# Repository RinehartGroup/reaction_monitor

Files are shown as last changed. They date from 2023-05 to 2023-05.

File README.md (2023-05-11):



# reaction_monitor
An Arduino-based data logger for logging temperature, gas flow, and gas composition data from chemical reactions.

## Motivation

Establishing meaningful trends and building physically meaningful models based on the analysis of nanomaterials requires that those materials be synthesized under carefully controlled, reproducible conditions. In many cases, however, the true reaction conditions are far more complex than is easily conveyed in the simplified narrative form of a publication experimental data section. In our initial trials of standardizing our raw data formats we isolated several key parameters of interest for real-time monitoring: reaction temperature, gas flow rate, and gas composition (for N<sub>2</sub>/O<sub>2</sub> mixtures). While such systems are likely common at scale, we sought to use readily available components (many of which are common in academic research labs or are otherwise low-cost) to automate data logging in a varatile and nominally modular fashion that would be amenable to a small-scale, rapidly changing research environment.

## Overview

<p align="center">
    reaction monitor setup
</p>

The heart of the reaction monitor is an Arduino Mega. The Arduino communicates with an [Omega PID controller](https://www.omega.ca/en/control-monitoring/controllers/pid-controllers/p/CN7200-Series) via its MODBUS serial interface. [Gas flow](https://www.mcmflow.com/product/model-100/) and [oxygen sensors](https://www.apogeeinstruments.com/so-110-soil-response-thermistor-reference-oxygen-sensor/) output 0 - 3.3 V signals which are read by [16-bit ADCs](https://www.adafruit.com/product/1085) and sent to the Arduino via the I2C protocol. 

Two oxygen sensors are available and are intended to be put before and after the reaction. In this initial implementation, a pure or mixed gas is bubbled throiugh through a solution containing the reactive species, such that the first oxygen sensor (OXY1) is calibrated under dry conditions and the second (OXY2) is calibrated under wet conditions. The Arduinio logs raw voltages from the sensors in addition to the calculated oxygen percentages, so oxygen percentages can always be recalculated during data workup (as is done in the [example data workup](sample_data_workup.ipynb)). The calibration procedure for the oxygen sensors are available in the [Apogee manual](assets/SO-100-200-manual.pdf), and our calibration data for both wet and dry conditions are available in [/calibration](calibration). The oxygen percentage calculations account for humidity. In our Arduino code, we assume 0% humidity for OXY1 as it measures a gas mixture directly from cylinders with dry gas. We placed a [temperature, pressure and humidty sensor](https://www.adafruit.com/product/2652) after OXY2 to calculate the post-reaction oxygen percentage. The humidity sensor is placed in a 3D printd enclosure available in [/materials](materials)

The electronics are housed in a 3D printed enclosure, also available in [/materials](materials). The enclosure includes two LCDs displaying basic information on oxygen percentages, gas flow rates, time, PID values (process value, set value, and output), and, when recording data, the name of the file being written. Data is recorded to a micro SD card. Recording is started/stopped by pressing the button on the front of the enclosure. When recording, a red LED will be lit and a blue LED will flash each time a data point is collected (which is every second in the current code).

<p align="center">
    labeled reaction monitor
</p>

## Example Usage

The [example data workup notebook](sample_data_workup.ipynb) uses data file [RXN00026.CSV](sample_data/RXN00026.CSV). This data was collected during a reaction which followed the procedure detailed in [Kirkpatrick _et al._ Size-Tunable Magnetite Nanoparticles from Well-Defined Iron Oleate Precursors, Chemistry of Materials, 2022](https://pubs.acs.org/doi/10.1021/acs.chemmater.2c02046) ([free copy here](https://drive.google.com/file/d/1hveF1zS2nrNvON7UYBfMMZ2yYlZfvH2g/view)). In short, the synthesis of magnetite nanoparticles uses a reduced pressure atmosphere, then an N<sub>2</sub> atmosphere during the initial heating of the reaction mixture. Once the reaction is under reflux a small amount of oxygen is introduced into the gas mixture. The size, shape, and presence/absence of core / shell structures involving wustite and magnetite can be affected by precise control of the gas flow, composition, and temperature profile. The reaction monitor records every aspect of these reaction conditions, including any user-intervention with the PID controller.

<p align="center">
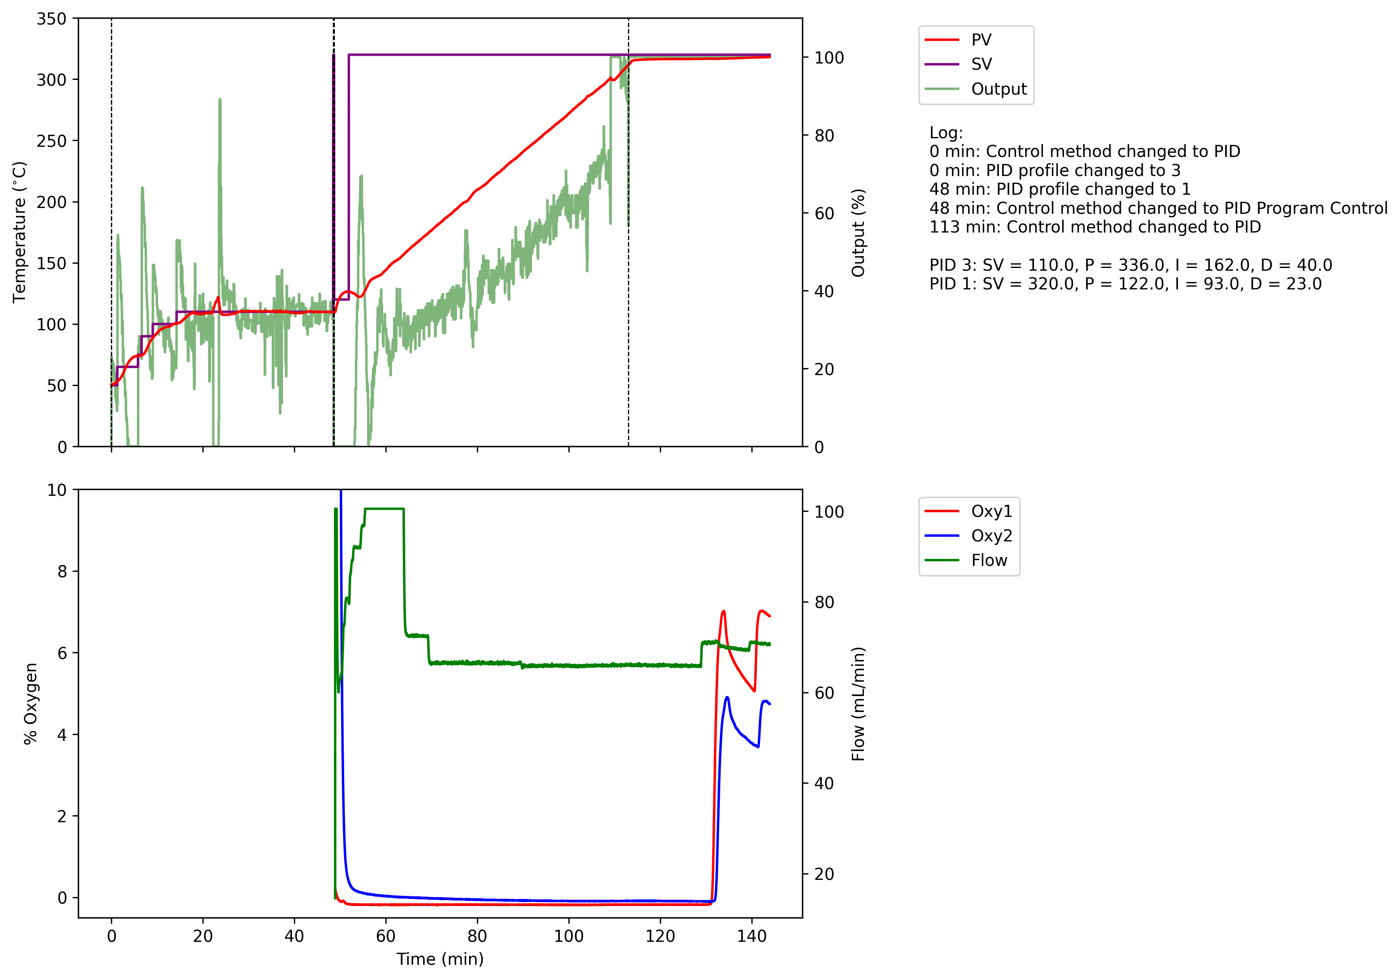
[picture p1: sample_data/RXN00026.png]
sample reaction data workup
    
</p>

## Future Work

While our primary goal was to provide automated data logging, initial data indicates the possibility of automating key decision points in chemical reactions, thus eliminating hidden sources of uncontrolled human intervention. In the usage example above, our results indicate that the timing of introducing O<sub>2</sub> into the reaction affects the phase purity of the final particles. Presently, O<sub>2</sub> is introduced when the chemist running the reaction visually detects the onset of solvent reflux. The data provided by the reaction monitor has the potential to solidify this association between O<sub>2</sub>, reflux, and particle quality and allow us to begin the process of optimizing an automatic trigger for flow adjustment. In this specific example, the trigger would be a function of the slope of the output tracking temperature control. This data corresponds to the power being used toward resistive heating (on a 0-100 scale). In the sample data, the start of reflux can be seen at the point where output is persistently at 100 and the process value (PV) is relatively constant and unable to reach the set value (SV) which is chosen to correspond to a temperature above the reflux temperature of the solution. Implementing this change would require replacing the passive gas sensors with mass flow controllers, allowing for both monitoring and control of the reaction conditions.

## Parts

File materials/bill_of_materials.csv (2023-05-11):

item | quantity | cost | link
Arduino Mega | 1 | 48.4 | https://store-usa.arduino.cc/products/arduino-mega-2560-rev3
16x2 LCD Display (I2C) | 2 | 11.99 | https://www.amazon.com/GeeekPi-Character-Backlight-Raspberry-Electrical/dp/B07S7PJYM6
DS3231 Precision RTC Breakout (I2C) | 1 | 17.5 | https://www.adafruit.com/product/3013
Micro SD Breakout Board (SPI) | 1 | 11.99 | https://www.amazon.com/FainWan-Storage-Expansion-Interface-Adapter/dp/B09JZC6TCD
ADS1115 16-Bit ADC - 4 Channel with Programmable Gain Amplifier (I2C) | 2 | 14.95 | https://www.adafruit.com/product/1085
BME280 I2C or SPI Temperature Humidity Pressure Sensor | 1 | 14.95 | https://www.adafruit.com/product/2652
LM2596 DC to DC Buck Converter | 1 | 8.99 | https://www.amazon.com/LM2596-Converter-3-0-40V-1-5-35V-Supply/dp/B08NV3JCBC
12V 2A AC Adapter | 1 | 11.99 | https://www.amazon.com/Adapter-Charger-Replacement-Regulated-Transformer/dp/B0852HX9HV
Apogee SO-110 Soil Response Thermistor Reference Oxygen Sensor | 2 | 365 | https://www.apogeeinstruments.com/so-110-soil-response-thermistor-reference-oxygen-sensor/
McMillan Flow Model 100-3 Gas Flow Sensor 20-100 mL/min | 1 | 275 | https://www.mcmflow.com/product/model-100/
McMillan Flow Model 100-5 Gas Flow Sensor 100-500 mL/min | 1 | 275 | https://www.mcmflow.com/product/model-100/
Omega CN7200 PID Controller | 1 |  | https://www.omega.ca/en/control-monitoring/controllers/pid-controllers/p/CN7200-Series
MD-30 CONN PLUG MALE MINI DIN 3P SLDR | 5 | 2.29 | https://www.digikey.com/en/products/detail/cui-devices/MD-30/96910
MD-30SP CONN RCPT FMALE MINI DIN 3P SLDR | 5 | 2.54 | https://www.digikey.com/en/products/detail/cui-devices/MD-30SP/165983
MD-70 CONN PLUG MALE MINI DIN 7P SLDR | 2 | 2.51 | https://www.digikey.com/en/products/detail/cui-devices/MD-70/96918
MD-70SP CONN RCPT FMALE MINI DIN 7P SLDR | 2 | 2.75 | https://www.digikey.com/en/products/detail/cui-devices/MD-70SP/135497
Barrel Jack Connector - Female | 1 | 9.99 | https://www.amazon.com/DaierTek-5-5x2-1mm-Female-Connector-Barrel/dp/B096XJWZJQ
Chemical-Resistant Gasket; Fluoroelastomer, for 1" Tube OD | 1 | 3.2 | https://www.mcmaster.com/5044K53/

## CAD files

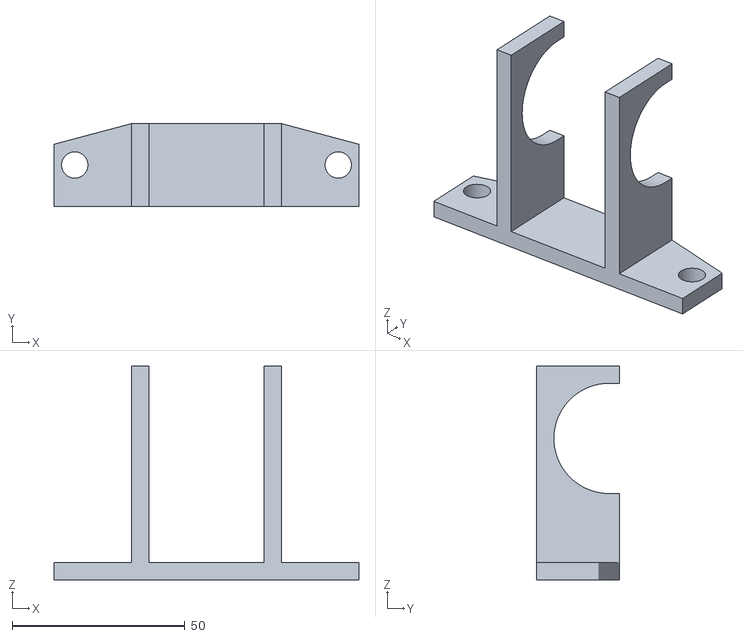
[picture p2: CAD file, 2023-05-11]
materials/humidity_sensor_housing_pegboard_adapter.stl
88.2 x 23.9 x 61.9

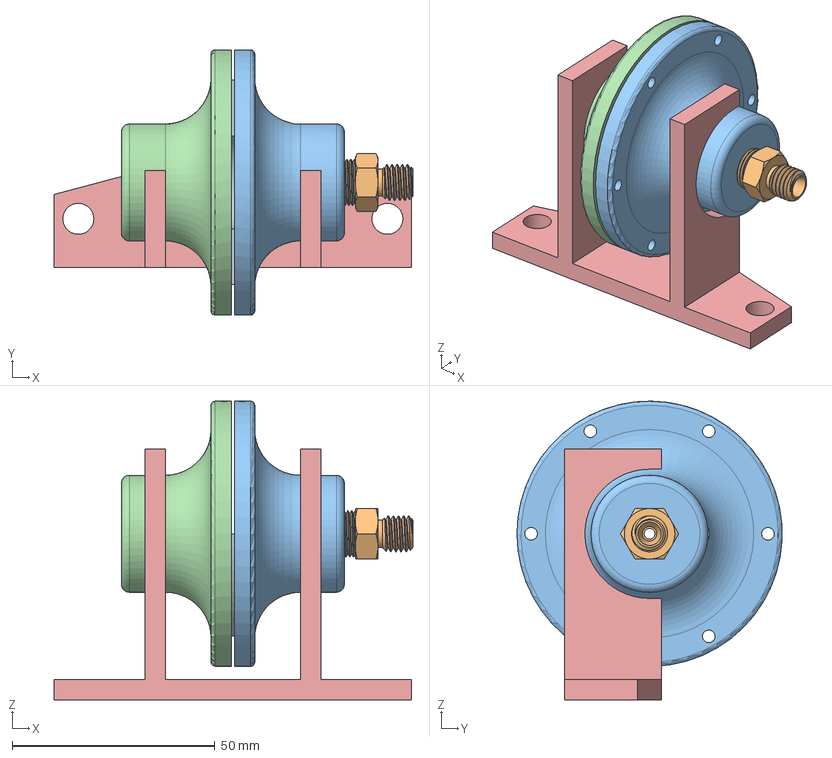
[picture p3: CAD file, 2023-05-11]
materials/humidity_sensor_housing.step
88.5 x 65.4 x 73.6 mm
5044K53_Chemical-Resistant Gasket
5272K292
scaled_part

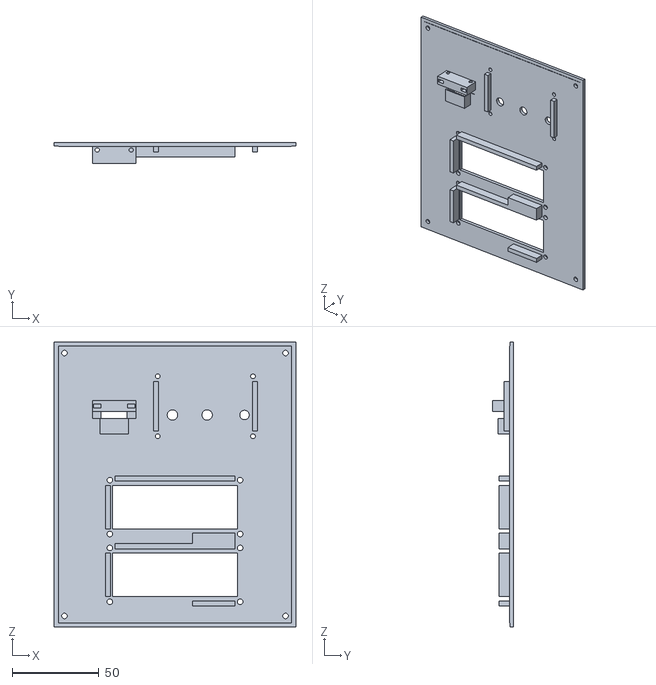
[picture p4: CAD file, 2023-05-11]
materials/reaction_monitor_enclosure_lid.stl
139.0 x 12.0 x 164.0

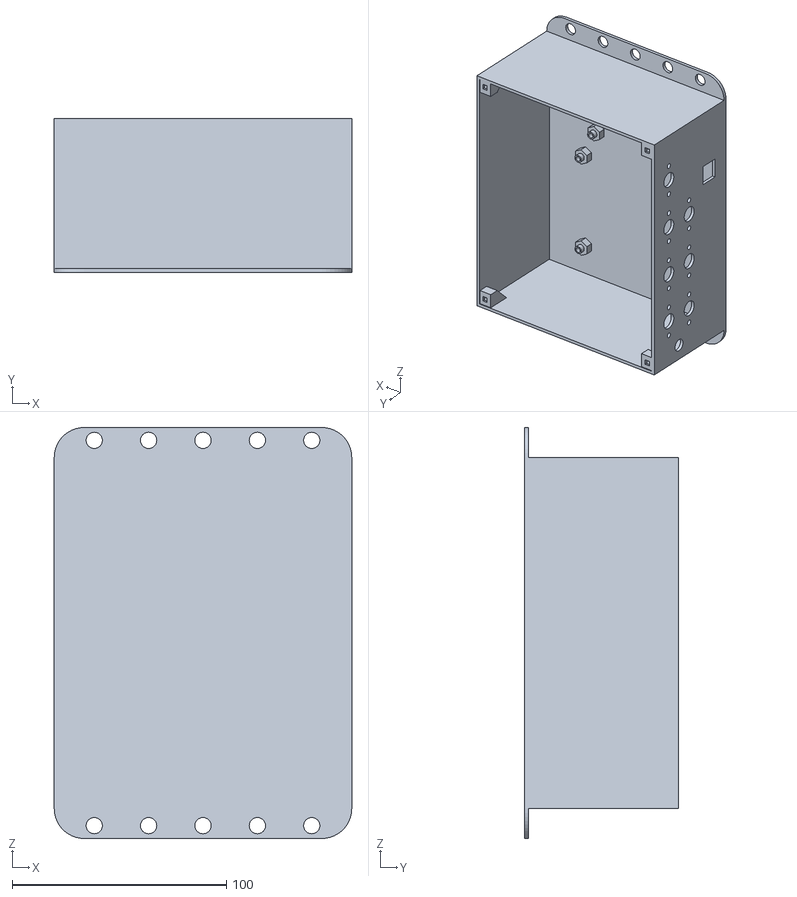
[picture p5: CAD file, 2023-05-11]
materials/reaction_monitor_enclosure_base.stl
139.0 x 72.0 x 192.0

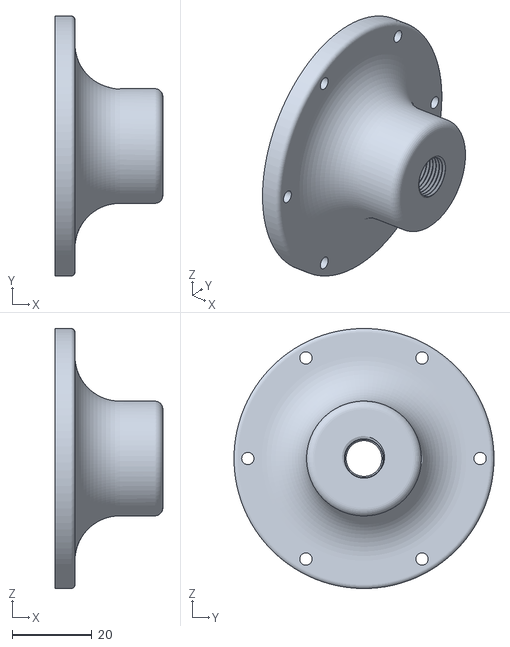
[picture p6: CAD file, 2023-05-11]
materials/humidity_sensor_housing_side1.stl
27.1 x 65.4 x 65.4

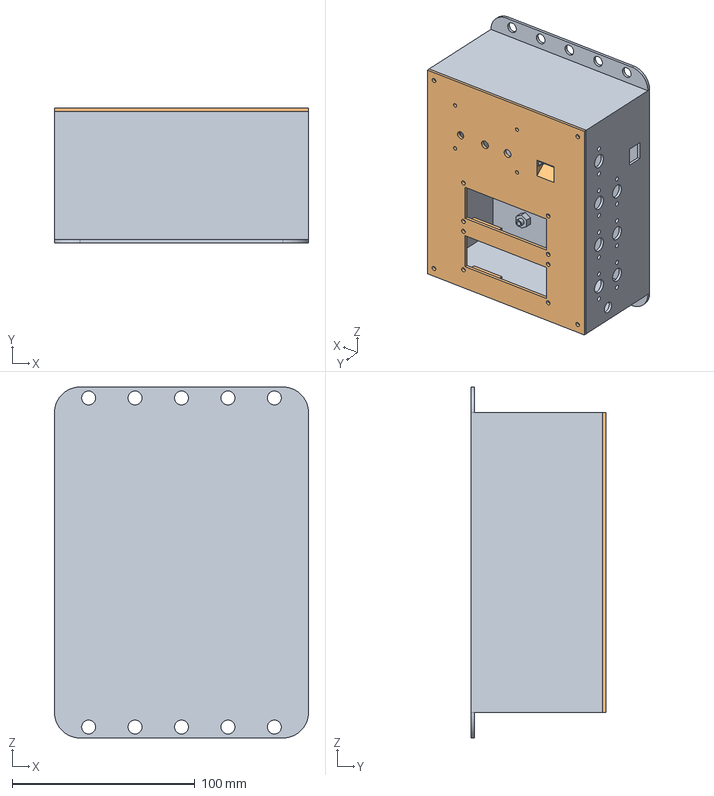
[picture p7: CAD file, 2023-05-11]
materials/reaction_monitor_enclosure.step
139.0 x 74.0 x 192.0 mm

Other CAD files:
materials/humidity_sensor_housing_side2.stl
materials/humidity_sensor_housing.f3z
materials/reaction_monitor_enclosure.f3d

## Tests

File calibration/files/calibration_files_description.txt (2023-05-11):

RXN00009.CSV; dry air; Sensors in sealed container with air and Drierite;
RXN00010.CSV; atmospheric; Sensors open to atmosphere;
RXN00011.CSV; wet air; Sensors in sealed container with water in bottom;
RXN00012.CSV; dry N2 no humidity sensor; Note: this had the humidity sensor unattached. Use RXN00016 instead;
RXN00015.CSV; wet N2; N2 stream through bubbler, then the two oxygen sensors, then the BME280 sensor;
RXN00016.CSV; dry N2; N2 stream straight to oxygen sensors then the BME280 sesnor;

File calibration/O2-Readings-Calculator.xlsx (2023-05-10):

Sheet: Sheet1
 | Sensor Model: SO- |  |  | Units |  | Yellow Cells = Requested Information
Calibration Info | Calibration mV Reading |  |  | mV
 | Calibration Air Temperature |  |  |  |  |  | SO-110, 120 Constants | SO-210, 220 Constants
 | Calibration Humidity |  |  | % |  | C1 | -0.06949 | -0.0361 | C3
 |  | Calibration Elevation |  |  |  | C2 | 0.001422 | 0.001896 | C2
 |  | Calibration Pressure |  | kPa |  | C3 | -8.213e-07 | -4.333e-06 | C1
Sample Info | Sample mV Reading |  |  | mV |  | Cal. Vapor Pressure |  | Sample Vapor Pressure
 | Sample Air Temperature |  |  |  |  | 0.000 |  | 0.000
 | Sample Humidity |  |  | % |  | Cal. Sat. Pressure |  | Samp. Sat Pressure
 |  | Sample Elevation |  |  |  | 0.152 |  | 0.152
 |  | Sample Pressure |  | kPa |  | Cal. Barr. Pressure |  | Samp. Barr. Pressure
Offset |  |  |  |  | 0.3 | 101.325 |  | 101.325
 |  |  |  |  |  | Calibration Temperature Coefficient
 |  |  |  |  |  | -1.265
Output and Correction Options
 | Calibration Factor (Multiplier) |  |  |  | -69.833 | CF = Correction Factor
 | Calibration Offset |  |  |  | 20.950 | mVc = mV at calibration
 |  |  |  |  |  | mV0 = mV at zero
 | Uncorrected Oxygen Reading [%] |  |  |  | 20.950 | CO = Calibration Offset
 |  |  |  |  |  | PB = Barrometric Pressure (kPa)
 |  |  |  |  |  | E = Elevation
 |  |  |  |  |  | O2 = Final O2 Reading
 |  |  |  |  |  | O2m = Uncorrected O2 Reading
 | Final Sample Oxygen Reading [%] |  |  |  | 20.950 | PBC = Barrometric Pressure (Calibration) [kPa]
Formulas for SO-110, 120, 210, 220 and Calculations |  |  |  |  |  | PBM = Barrometric Pressure (Sample) [kPa]
 |  |  |  |  |  | TS = Air Temperature (Sample)
 |  |  |  |  |  | TC = Air Temperature (Calibration)
 |  |  |  |  |  | C1 = Temperature Constant 1
 |  |  |  |  |  | C2 = Temperature Constant 2
 |  |  |  |  |  | C3 = Temperature Constant 3
 |  |  |  |  |  | eAM = Vapor Pressure (Sample)
 |  |  |  |  |  | eAC = Vapor Pressure (Calibration)
 |  |  |  |  |  | eA = Vapor Pressure
 |  |  |  |  |  | eS = Saturation Vapro Pressure
 |  |  |  |  |  | RH = Relative Humidity
 |  |  |  |  |  | TA = Air Temperature
 | FALSE
 | FALSE | FALSE
 | FALSE
1 | FALSE | FALSE | TRUE | FALSE
 |  | FALSE | FALSE
 | FALSE
 | FALSE | FALSE
 | FALSE
1 | FALSE | FALSE | TRUE | FALSE
 |  | FALSE | FALSE
1 | TRUE
 | FALSE
TRUE
TRUE
TRUE

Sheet: Sheet2
86.7043439

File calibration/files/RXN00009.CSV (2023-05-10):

File Name | rxn00009.csv
Date | 2022-05-12 18:10:19
[DATA]
time (s) | oxy1_voltage (V) | oxy1_O2 (%) | oxy1_temp_voltage (V) | oxy1_temp (C) | oxy2_voltage (V) | oxy2_O2 (%) | oxy2_temp_voltage (V) | oxy2_temp (C) | bme_temp (C) | pressure (kPa) | humidity (%) | flow1_voltage (V) | flow1_flow (mL/min) | flow2_voltage (V) | flow2_flow (mL/min) | PV (C) | SV (C) | Control Method | Output | PID profile | PID SV | P | I | D
1652379029 | 0.052000 | 21.32 | 1.023000 | 23.14 | 0.049266 | 20.17 | 1.030000 | 22.92 | 21.30 | 100.16 | 53.83 | 2.856445 | 57.53 | 2.709961 | 271.41 | 0.00 | 0.00 | 0 | 0 | 0 | 0.00 | 0 | 0 | 0
1652379039 | 0.051984 | 21.32 | 1.024375 | 23.10 | 0.049266 | 20.17 | 1.029125 | 22.95 | 21.30 | 100.17 | 53.82 | 1.674805 | 33.78 | 1.562500 | 160.47 | 0.00 | 0.00 | 0 | 0 | 0 | 0.00 | 0 | 0 | 0
1652379049 | 0.051969 | 21.31 | 1.025625 | 23.06 | 0.049250 | 20.17 | 1.027875 | 22.99 | 21.30 | 100.15 | 49.57 | 2.690430 | 54.20 | 2.548828 | 255.83 | 0.00 | 0.00 | 0 | 0 | 0 | 0.00 | 0 | 0 | 0
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

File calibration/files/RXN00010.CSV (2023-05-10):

File Name | rxn00010.csv
Date | 2022-05-13 09:28:20
[DATA]
time (s) | oxy1_voltage (V) | oxy1_O2 (%) | oxy1_temp_voltage (V) | oxy1_temp (C) | oxy2_voltage (V) | oxy2_O2 (%) | oxy2_temp_voltage (V) | oxy2_temp (C) | bme_temp (C) | pressure (kPa) | humidity (%) | flow1_voltage (V) | flow1_flow (mL/min) | flow2_voltage (V) | flow2_flow (mL/min) | PV (C) | SV (C) | Control Method | Output | PID profile | PID SV | P | I | D
1652434110 | 0.052969 | 21.77 | 1.057875 | 22.05 | 0.050578 | 20.77 | 1.036250 | 22.73 | 21.52 | 100.00 | 36.19 | 1.625977 | 32.80 | 1.508789 | 155.28 | 0.00 | 0.00 | 0 | 0 | 0 | 0.00 | 0 | 0 | 0
1652434120 | 0.052906 | 21.75 | 1.057250 | 22.07 | 0.050531 | 20.75 | 1.035000 | 22.77 | 21.59 | 100.00 | 38.09 | 2.617187 | 52.72 | 2.431641 | 244.50 | 0.00 | 0.00 | 0 | 0 | 0 | 0.00 | 0 | 0 | 0
1652434130 | 0.052703 | 21.66 | 1.057125 | 22.08 | 0.050328 | 20.66 | 1.034250 | 22.79 | 21.64 | 100.00 | 37.37 | 1.591797 | 32.11 | 1.489258 | 153.39 | 0.00 | 0.00 | 0 | 0 | 0 | 0.00 | 0 | 0 | 0
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

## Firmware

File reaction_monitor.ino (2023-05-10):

#include <Wire.h>
#include <RTClib.h>
#include <LiquidCrystal_I2C.h>
#include <Adafruit_ADS1X15.h>
#include <Adafruit_BME280.h>
#include <math.h>
#include <AltSoftSerial.h>
#include <SensorModbusMaster.h>
#include <SPI.h>
#include <SD.h>

bool CALIBRATE = false;

RTC_DS3231 rtc;

#define updateInterval 1000 // 1000 ms for actual use, 10000 ms for calibration
unsigned long lastUpdate = 0;

#define BUTTON_PIN 2
#define RECORDING_LED 3
int ledState = LOW;
int buttonState;
int lastButtonState = HIGH;
bool recording = false;
unsigned long lastDebounceTime = 0;
unsigned long debounceDelay = 50;

#define flow1 A0 // model 100-3, range 20-100 mL/min, SN 46747
#define flow2 A1 // model 100-5, range 100-500 mL/min, SN 47499
#define FLOW1_CAL_SLOPE 20.103417415227547
#define FLOW1_CAL_INTERCEPT 0.10905233849315721
#define FLOW2_CAL_SLOPE 96.6787554876885
#define FLOW2_CAL_INTERCEPT 9.410192784882554

Adafruit_ADS1115 oxy;
Adafruit_ADS1115 oxyTemp;
Adafruit_BME280 bme;

#define OXY_RES 2.0 * 0.512 / 65536.0      // GAIN_EIGHT
#define OXY_TEMP_RES 2.0 * 4.096 / 65536.0 // GAIN_ONE

#define PCAL1 99.99825        // kPa
#define HCAL1 4.75015         // %, dry calibration
#define OXY1_VCAL 0.052950695 // V
#define OXY1_V0 0.001456225   // V
#define OXY1_TCAL 22.02595    // °C
#define PCAL2 100.044045      // kPa
#define HCAL2 100.0           // %, wet calibration
#define OXY2_VCAL 0.04897935  // V
#define OXY2_V0 0.00153704    // V
#define OXY2_TCAL 23.3594     // °C

float OXY1_CAL[5] = {PCAL1, HCAL1, OXY1_VCAL, OXY1_V0, OXY1_TCAL}; // SN 6089
float OXY2_CAL[5] = {PCAL2, HCAL2, OXY2_VCAL, OXY2_V0, OXY2_TCAL}; // SN 6238

// input variables
DateTime now;
int16_t oxy1_adc, oxy1_temp_adc, oxy2_adc, oxy2_temp_adc;
int16_t flow1_adc, flow2_adc;
float bme_temp, pressure, humidity;
// calculated variables
float oxy1_percent, oxy1_temp, oxy2_percent, oxy2_temp;
float flow1_mLmin, flow2_mLmin;

// LCD display
LiquidCrystal_I2C lcd_omega(0x26, 16, 2);
LiquidCrystal_I2C lcd_gas(0x27, 16, 2);

/*
Modbus communication with Omega PID controller
pins:
altsoftserial: Tx: 9, Rx: 8

Temperature Controller Settings:
CoSH on
C-SL rtU
C-no 2
bPS 9600
LEn 8
PrtY nonE
StoP 1
*/

#define OMEGA_ADDRESS 0x02
#define MODBUS_BAUD 9600

AltSoftSerial modbusSerial; // uses 8N1
modbusMaster omega;

// Omega parameters
#define READ_REGISTER 0x03
#define PV_ADDR 0x1000
#define SV_ADDR 0x1001
#define CTRL_METHOD_ADDR 0x1005
#define OUT_ADDR 0x1012
#define PID_NUM_ADDR 0x101C
#define PID_SV_ADDR 0x101D
#define P_ADDR 0x1009
#define I_ADDR 0x100A
#define D_ADDR 0x100B

float omega_pv = 0.0, omega_sv = 0.0, omega_pid_sv = 0.0;
int omega_ctrl_method = 0, omega_out = 0, omega_pid_num = 0, omega_p = 0, omega_i = 0, omega_d = 0;
bool omega_connected = false;

/* SD card
pins:
    - MISO, 50
    - MOSI, 51
    - SCK, 52
    - SS, 53
*/
#define SD_CS 53
String fileName = "rxn00001.csv";

void setup()
{
    Serial.begin(9600);

    rtc.begin();

    pinMode(BUTTON_PIN, INPUT_PULLUP);
    pinMode(RECORDING_LED, OUTPUT);
    digitalWrite(RECORDING_LED, ledState);

    // OXYGEN SENSORS
    oxy.begin(0x48);     // the O2 sensors of the two Apogee S110 sensors
    oxyTemp.begin(0x49); // the temperature sensor of the two Apogee S110 sensors
    oxy.setGain(GAIN_EIGHT);
    oxyTemp.setGain(GAIN_ONE);

    pinMode(flow1, INPUT);
    pinMode(flow2, INPUT);

    // TEMP/PRESSURE/HUMIDITY SENSORS
    bme.begin();

    // LCD DISPLAY
    lcd_omega.init();
    lcd_omega.backlight();
    lcd_omega.clear();
    lcd_gas.init();
    lcd_gas.backlight();
    lcd_gas.clear();

    // MODBUS COMMUNICATION
    modbusSerial.begin(MODBUS_BAUD);
    omega.begin(OMEGA_ADDRESS, modbusSerial);

    omega_pv = omega.uint16FromRegister(READ_REGISTER, PV_ADDR, bigEndian) / 10.0;
    if (omega_pv != 0.0)
    {
        omega_connected = true;
        Serial.println("Omega PID controller connected");
    }
    else
    {
        omega_connected = false;
        Serial.println("Omega PID controller not connected");
    }

    // SD CARD
    bool cardOK = true;
    Serial.print("Initializing SD card...");
    // see if the card is present and can be initialized:
    if (!SD.begin(SD_CS))
    {
        Serial.println("Card failed, or not present");
        cardOK = false;
    }
    if (cardOK)
    {
        Serial.println("card initialized.");
    }
}

void loop()
{
    int buttonReading = digitalRead(BUTTON_PIN);
    if (buttonReading != lastButtonState)
    {
        lastDebounceTime = millis();
    }
    if ((millis() - lastDebounceTime) > debounceDelay)
    {
        if (buttonReading != buttonState)
        {
            buttonState = buttonReading;
            if (buttonState == LOW)
            {
                ledState = !ledState;
                digitalWrite(RECORDING_LED, ledState);
                recording = !recording;
                if (recording == true)
                {
                    fileName = formatFileName();
                    Serial.print("start recording to ");
                    Serial.println(fileName);
                    writeHeader(fileName);
                }
                else if (recording == false)
                {
                    Serial.print("stop recording to ");
                    Serial.println(fileName);
                }
            }
        }
    }
    lastButtonState = buttonReading;

    if ((millis() - lastUpdate) > updateInterval)
    {
        lastUpdate = millis();
        now = rtc.now();

        oxy1_adc = oxy.readADC_Differential_0_1(); // oxy1 sensor: Apogee SO-110, SN 6089
        oxy1_temp_adc = oxyTemp.readADC_Differential_0_1();
        oxy2_adc = oxy.readADC_Differential_2_3(); // oxy2 sensor: Apogee SO-110, SN 6238
        oxy2_temp_adc = oxyTemp.readADC_Differential_2_3();

        bme_temp = bme.readTemperature();
        pressure = bme.readPressure() / 1000.0F;
        humidity = bme.readHumidity();

        oxy1_temp = Convert_Oxy_Temp_adc(oxy1_temp_adc);
        oxy2_temp = Convert_Oxy_Temp_adc(oxy2_temp_adc);
        oxy1_percent = Convert_Oxy_adc(oxy1_adc, oxy1_temp, pressure, 0.0, OXY1_CAL); // assume 0% humidity coming the O2/N2 gas tanks
        oxy2_percent = Convert_Oxy_adc(oxy2_adc, oxy2_temp, pressure, humidity, OXY2_CAL);

        flow1_adc = analogRead(flow1);
        flow2_adc = analogRead(flow2);

        flow1_mLmin = Convert_Flow_adc(flow1_adc, FLOW1_CAL_SLOPE, FLOW1_CAL_INTERCEPT);
        flow2_mLmin = Convert_Flow_adc(flow2_adc, FLOW2_CAL_SLOPE, FLOW2_CAL_INTERCEPT);

        // read Omega controller
        if (omega_connected)
        {
            omega_pv = omega.uint16FromRegister(READ_REGISTER, PV_ADDR, bigEndian) / 10.0;
            omega_sv = omega.uint16FromRegister(READ_REGISTER, SV_ADDR, bigEndian) / 10.0;
            omega_ctrl_method = omega.uint16FromRegister(READ_REGISTER, CTRL_METHOD_ADDR, bigEndian);
            omega_out = omega.uint16FromRegister(READ_REGISTER, OUT_ADDR, bigEndian);
            omega_pid_num = omega.uint16FromRegister(READ_REGISTER, PID_NUM_ADDR, bigEndian);
            omega_pid_sv = omega.uint16FromRegister(READ_REGISTER, PID_SV_ADDR, bigEndian) / 10.0;
            omega_p = omega.uint16FromRegister(READ_REGISTER, P_ADDR, bigEndian);
            omega_i = omega.uint16FromRegister(READ_REGISTER, I_ADDR, bigEndian);
            omega_d = omega.uint16FromRegister(READ_REGISTER, D_ADDR, bigEndian);
        }

        // update LCDs
        lcd_omega.clear();
        lcd_omega.setCursor(0, 0);
        lcd_omega.print(formatDigits(now.hour()));
        lcd_omega.print(":");
        lcd_omega.print(formatDigits(now.minute()));
        lcd_omega.print(":");
        lcd_omega.print(formatDigits(now.second()));
        if (recording)
        {
            lcd_omega.setCursor(11, 0);
            String rxnNum = fileName;
            rxnNum.remove(0, 3);
            rxnNum.remove(rxnNum.length() - 4);
            lcd_omega.print(rxnNum);
        }
        if (CALIBRATE)
        {
            lcd_omega.setCursor(0, 1);
            lcd_omega.print(String(bme_temp, 1));
            lcd_omega.setCursor(5, 1);
            lcd_omega.print(String(pressure, 1));
            lcd_omega.setCursor(12, 1);
            lcd_omega.print(String(humidity, 1));
        }
        else
        {
            lcd_omega.setCursor(0, 1);
            lcd_omega.print(String(omega_pv, 1));
            lcd_omega.setCursor(5, 1);
            lcd_omega.print(String(omega_sv, 1));
            lcd_omega.setCursor(13, 1);
            lcd_omega.print(omega_out);
        }
        lcd_gas.clear();
        lcd_gas.setCursor(0, 0);
        lcd_gas.print("Ox%: ");
        lcd_gas.print(String(oxy1_percent, 1));
        lcd_gas.print(" ");
        lcd_gas.print(String(oxy2_percent, 1));
        lcd_gas.setCursor(0, 1);
        if (CALIBRATE)
        {
            lcd_gas.print(oxy1_adc * OXY_RES, 5);
            lcd_gas.print("  ");
            lcd_gas.print(oxy2_adc * OXY_RES, 5);
        }
        else
        {
            lcd_gas.print("Flow: ");
            lcd_gas.print(String(flow1_mLmin, 1));
            lcd_gas.print(" ");
            lcd_gas.print(String(flow2_mLmin, 1));
        }

        Print_Report();

        if (recording)
        {
            writeData(fileName);
        }
    }
}

void Print_Report()
{
    Serial.print(now.unixtime());
    Serial.print(" ");
    Serial.print(recording);
    Serial.print(" ");
    Serial.print(oxy1_adc * OXY_RES, 6);
    Serial.print(" ");
    Serial.print(oxy1_percent);
    Serial.print(" ");
    Serial.print(oxy1_temp_adc * OXY_TEMP_RES, 6);
    Serial.print(" ");
    Serial.print(oxy1_temp);
    Serial.print(" ");
    Serial.print(oxy2_adc * OXY_RES, 6);
    Serial.print(" ");
    Serial.print(oxy2_percent);
    Serial.print(" ");
    Serial.print(oxy2_temp_adc * OXY_TEMP_RES, 6);
    Serial.print(" ");
    Serial.print(oxy2_temp);
    Serial.print(" ");
    Serial.print(bme_temp);
    Serial.print(" ");
    Serial.print(pressure);
    Serial.print(" ");
    Serial.print(humidity);
    Serial.print(" ");
    Serial.print(flow1_adc * 5.0 / 1024.0, 6);
    Serial.print(" ");
    Serial.print(flow1_mLmin);
    Serial.print(" ");
    Serial.print(flow2_adc * 5.0 / 1024.0, 6);
    Serial.print(" ");
    Serial.print(flow2_mLmin);
    Serial.print(" ");
    Serial.print(omega_pv);
    Serial.print(" ");
    Serial.print(omega_sv);
    Serial.print(" ");
    Serial.print(omega_ctrl_method);
    Serial.print(" ");
    Serial.print(omega_out);
    Serial.print(" ");
    Serial.print(omega_pid_num);
    Serial.print(" ");
    Serial.print(omega_pid_sv);
    Serial.print(" ");
    Serial.print(omega_p);
    Serial.print(" ");
    Serial.print(omega_i);
    Serial.print(" ");
    Serial.print(omega_d);
    Serial.println();
}

// OXYGEN SENSOR FUCTIONS
float Convert_Oxy_adc(int16_t adc, float temp, float pressure, float humidity, float OXY_CAL[])
{
    // OXY_CAL = {PCAL, HCAL, OXY_VCAL, OXY_V0, OXY_TCAL}
    float v = adc * OXY_RES;
    float CF = (0.2095 * OXY_CAL[0]) / (OXY_CAL[2] - OXY_CAL[3]);
    float oxy_percent = CF * (v - OXY_CAL[3]);
    // pressure adjustment
    oxy_percent = oxy_percent * (OXY_CAL[0] / pressure);
    // humidity adjustment
    float sat_vp = 0.61121 * exp((temp * (18.678 - temp / 234.5)) / (257.14 + temp));
    float cal_sat_vp = 0.61121 * exp((OXY_CAL[4] * (18.678 - OXY_CAL[4] / 234.5)) / (257.14 + OXY_CAL[4]));
    float vp = sat_vp * humidity / 100.0;
    float cal_vp = cal_sat_vp * OXY_CAL[2] / 100.0;
    oxy_percent = oxy_percent * ((OXY_CAL[0] + vp - cal_vp) / OXY_CAL[0]);
    // temperature adjustment
    float c1 = -6.949e-2, c2 = 1.422e-3, c3 = -8.213e-7;
    oxy_percent = oxy_percent + c3 * pow(temp, 3) + c2 * pow(temp, 2) + c1 * temp - c3 * pow(OXY_CAL[4], 3) - c2 * pow(OXY_CAL[4], 2) - c1 * OXY_CAL[4];
    return oxy_percent;
}

float sat_vapor_pressure(float temp)
{
    // note: temp in C
    float vp = 0.61121 * exp((temp * (18.678 - temp / 234.5)) / (257.14 + temp));
}
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

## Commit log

2023-05-11 documentation and workup update
    [RXN00026.CSV, bill_of_materials.csv, humidity_sensor_housing.f3z, humidity_sensor_housing.step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]
2023-05-11 bill of materials update
    [bill_of_materials.csv]
